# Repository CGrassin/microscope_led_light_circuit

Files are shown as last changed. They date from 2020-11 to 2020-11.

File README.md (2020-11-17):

# Microscope LED Driver circuit

This circuit drives a 1W or 3W LED to convert old optical microscopes from light bulb/halogen lamp to LED ligthing.

It is powered from a USB type C port and is fully dimmable. It may be used with a USB power bank, for instance.

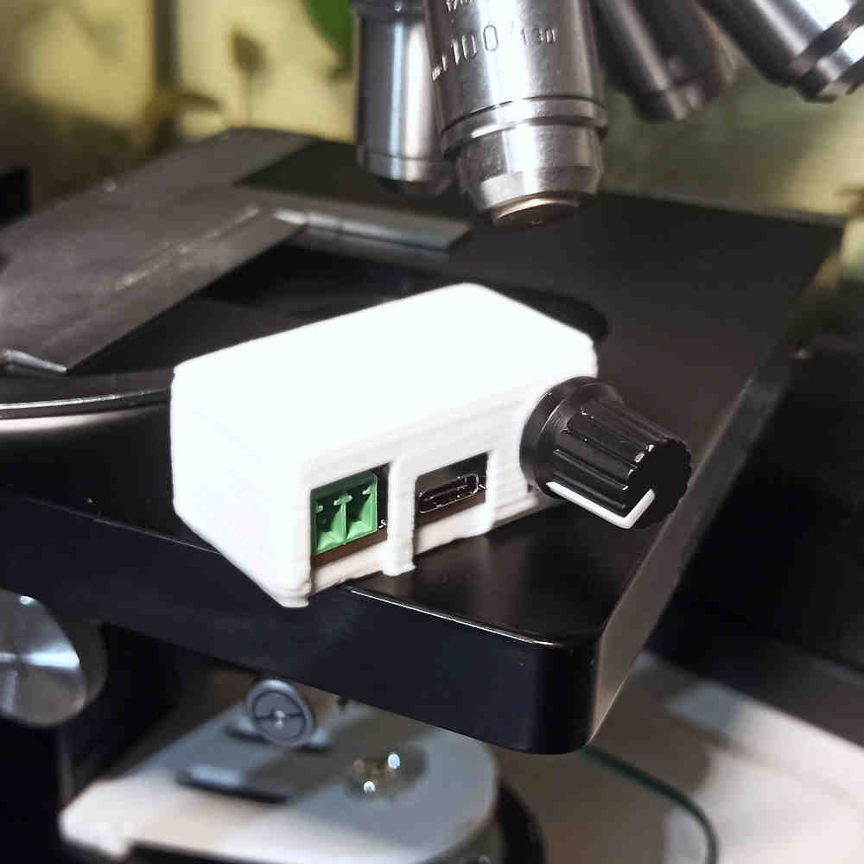
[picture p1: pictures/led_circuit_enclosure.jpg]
LED dimming circuit in its 3D printed enclosure


LEDs are considerably more efficient (i.e. less heat), have a longer lifespan and have a better color accuracy than bulbs. My circuit has a high PWM frequency to avoid flickering and rolling bands effect in photographs.

## Features

| Specification  | Value                                     |
|:---------------|:------------------------------------------|
| Power input    | 5V @ 1A max. (USB type C)                 |
| PWM frequency  | >8KHz                                     |
| Controls       | Combined knob dimming (0-100%) and ON/OFF |
| Estimated cost | About $10                                 |

## Build instructions

Gerber files are ready to upload to your prefered PCB manufacturer. The components are generic and should be available at most electronic components distributors. I personally use JLCPCB and LCSC.

Hand soldering this board is easy. I included an "interactive BOM" to help with part placement.

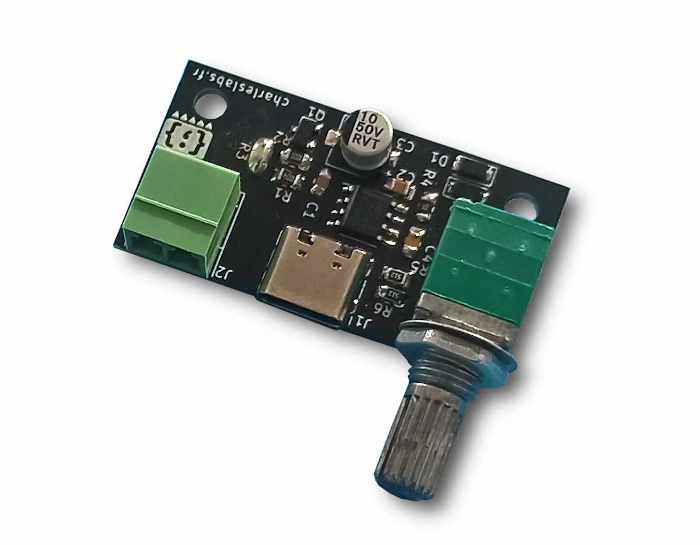
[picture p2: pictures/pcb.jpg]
This project's PCB fully assembled


The only additional required parts are a 1W or 3W "star" LED with a 30° lens to pre-focus the light into the condenser. Thank to this lens, a 1W LED is sufficient. You can choose your favorite color temperature.

I also included a 3D-printable case for the circuit. Print at 0.2mm layer height, no support required.

*Although I designed a PCB, this circuit could be build on a piece of stripboard or even breadboard.*

## Principle of operation

This circuit uses a classic 555 variable duty cycle astable multivibrator configuration.

The potentiometer adjusts the charge and discharge rate of the TRIG capacitor. The frequency of the carrier depend on the RC constant of those parts.

## License

All files in this repository are released under CC-BY license.

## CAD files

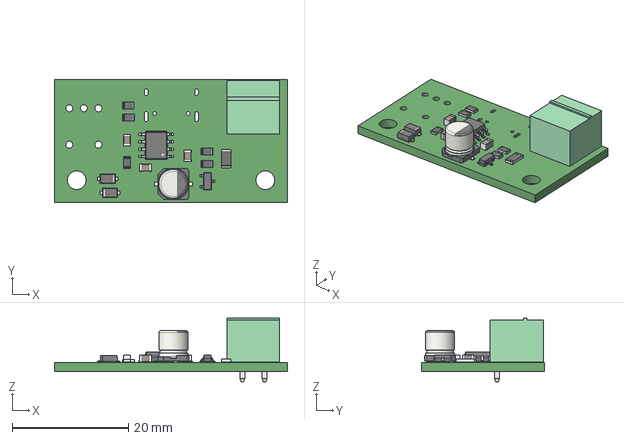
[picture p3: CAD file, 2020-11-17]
Microscope_LED_light_enclosure/Microscope_LED.step
40.0 x 21.1 x 10.9 mm

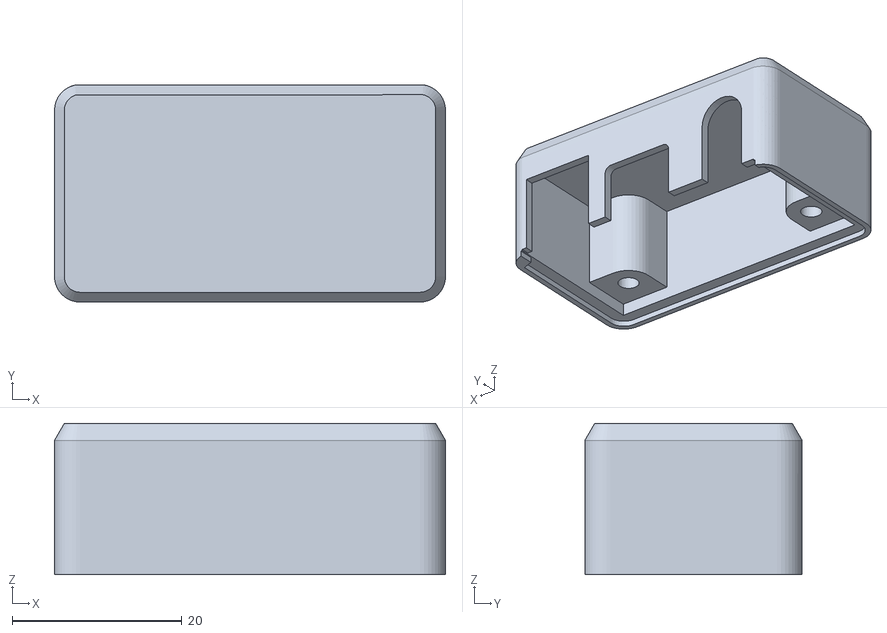
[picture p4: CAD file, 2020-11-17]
Microscope_LED_light_enclosure/Microscope_LED-TOP.STL
46.0 x 25.6 x 17.8

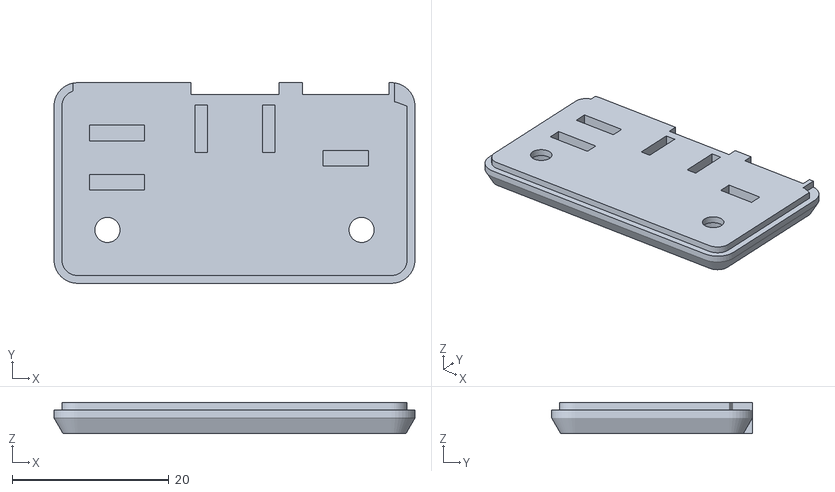
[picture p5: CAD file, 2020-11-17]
Microscope_LED_light_enclosure/Microscope_LED-BASE.STL
46.0 x 25.6 x 4.00

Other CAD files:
Microscope_LED_light_enclosure/Microscope_LED.SLDPRT

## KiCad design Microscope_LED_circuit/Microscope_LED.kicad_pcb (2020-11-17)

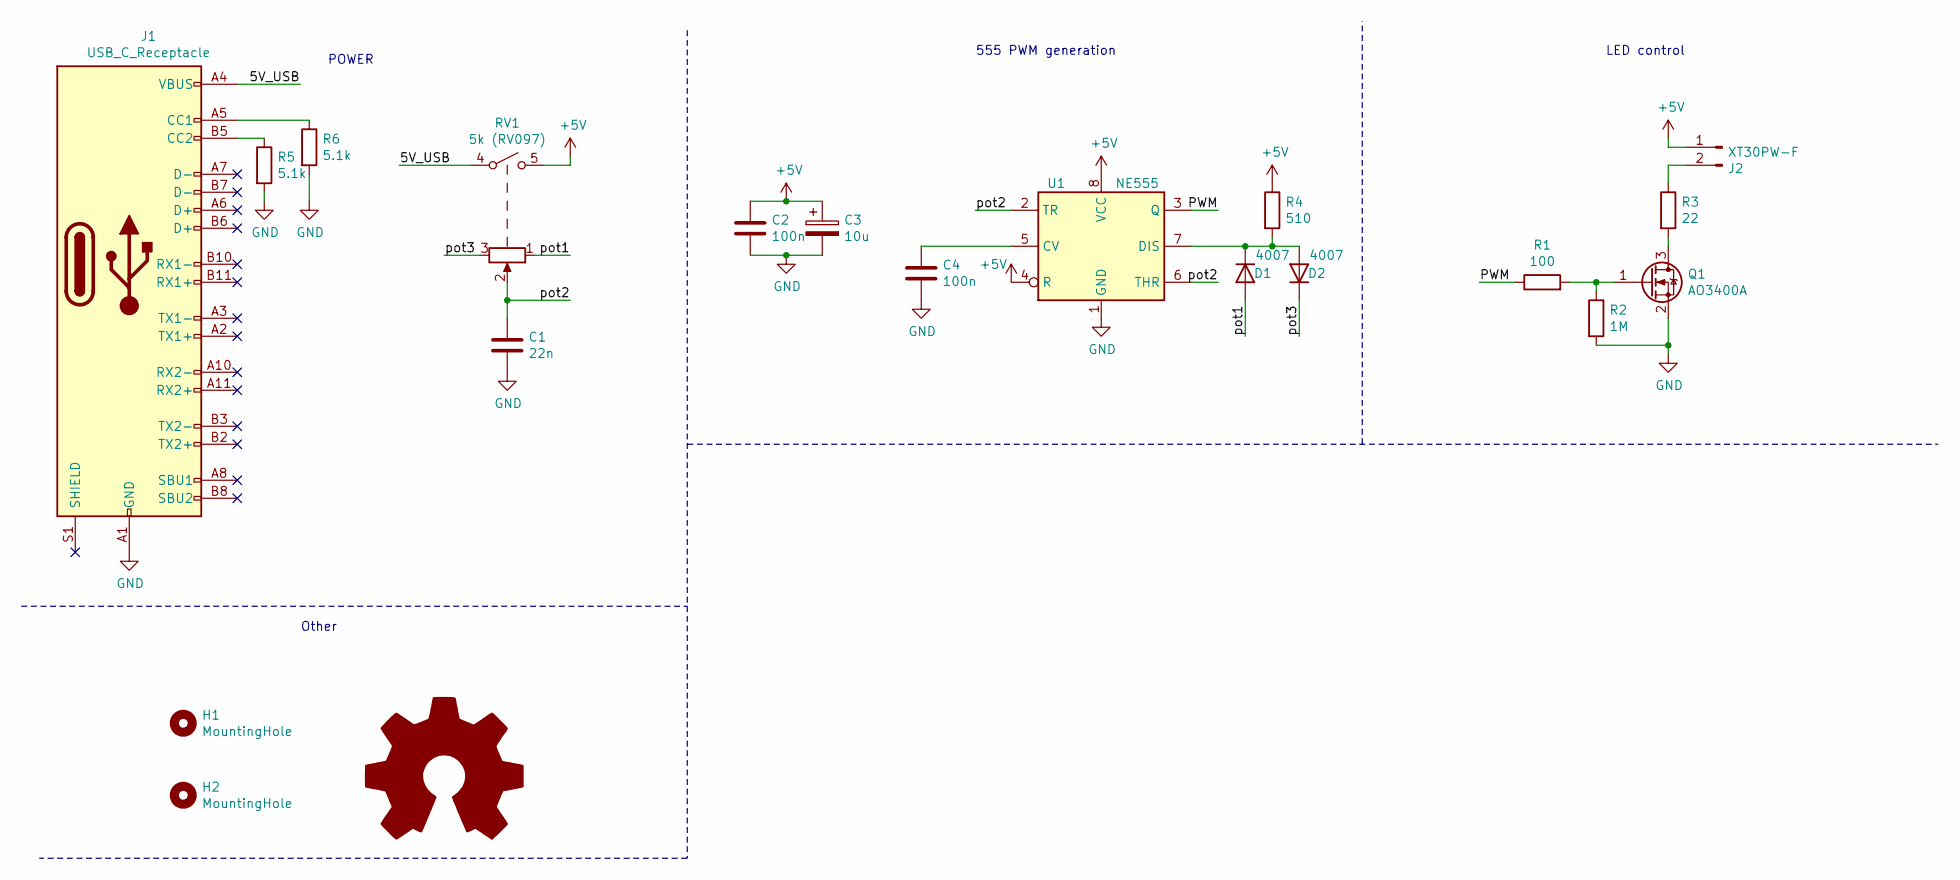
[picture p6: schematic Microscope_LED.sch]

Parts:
C1: 22n; C_0805_2012Metric_Pad1.15x1.40mm_HandSolder; LCSC C282752
C2, C4: 100n; C_0805_2012Metric_Pad1.15x1.40mm_HandSolder; LCSC C476766
C3: 10u; CP_Elec_5x5.4; LCSC C72487
D1, D2: 4007; D_SOD-123F; LCSC C108803
H1, H2: MountingHole; MountingHole_3.2mm_M3
J1: USB_C_Receptacle; USB_C_Receptacle_HRO_TYPE-C-31-M-12; LCSC C393939
J2: XT30PW-F; PhoenixContact_MC_1,5_2-G-3.81_1x02_P3.81mm_Horizontal; LCSC C8387
LOGO1: Logo_Open_Hardware_Large; Charleslabs_Logo_5mm
Q1: AO3400A; SOT-23; LCSC C122850
R1: 100; R_0805_2012Metric_Pad1.15x1.40mm_HandSolder; LCSC C17408
R2: 1M; R_0805_2012Metric_Pad1.15x1.40mm_HandSolder; LCSC C17514
R3: 22; R_1206_3216Metric
R4: 510; R_0805_2012Metric_Pad1.15x1.40mm_HandSolder; LCSC C25317
R5, R6: 5.1k; R_0805_2012Metric_Pad1.15x1.40mm_HandSolder; LCSC C115337
RV1: 5k (RV097); RV097
U1: NE555; SOIC-8_3.9x4.9mm_P1.27mm; LCSC C7593

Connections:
+5V: C2.1, C3.1, J2.1, R4.1, RV1.5, U1.4 (R), U1.8 (VCC)
/5V_USB: J1.A4 (VBUS), J1.A9 (VBUS), J1.B4 (VBUS), J1.B9 (VBUS), RV1.4
/PWM: R1.1, U1.3 (Q)
/pot1: D1.2 (A), RV1.1
/pot2: C1.1, RV1.2, U1.2 (TR), U1.6 (THR)
/pot3: D2.1 (K), RV1.3
GND: C1.2, C2.2, C3.2, C4.2, J1.A1 (GND), J1.A12 (GND), J1.B1 (GND), J1.B12 (GND), Q1.2 (S), R2.2, R5.2, R6.2, U1.1 (GND)
unnamed: C4.1, U1.5 (CV)
unnamed: D1.1 (K), D2.2 (A), R4.2, U1.7 (DIS)
unnamed: J1.A5 (CC1), R6.1
unnamed: J1.B5 (CC2), R5.1
unnamed: J2.2, R3.1
unnamed: Q1.1 (G), R1.2, R2.1
unnamed: Q1.3 (D), R3.2

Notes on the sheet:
POWER
555 PWM generation
LED control
Other

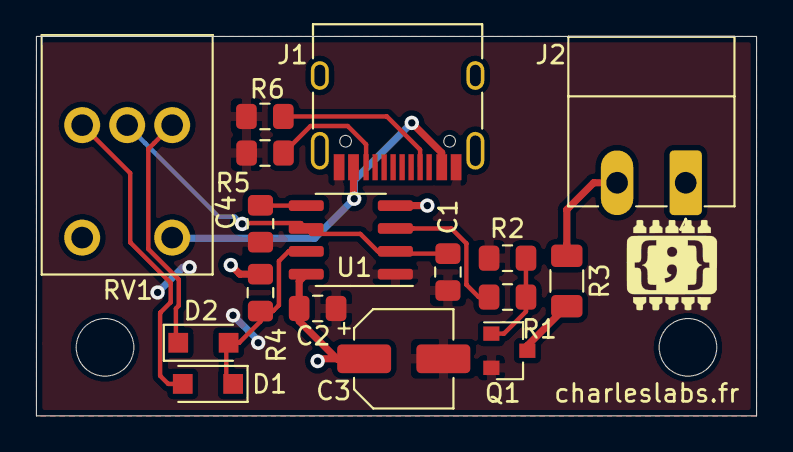
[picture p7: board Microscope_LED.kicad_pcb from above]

Board: 2 copper layers, 40.0 x 21.1 mm, 20 parts (0 on the bottom side), 14 nets.

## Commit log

2020-11-17 Release PCB rev. 1
    [Microscope_LED-B_Cu.gbr, Microscope_LED-B_Mask.gbr, Microscope_LED-B_Paste.gbr, Microscope_LED-B_SilkS.gbr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]
2020-11-17 Release PCB rev. 2
    [Microscope_LED-B_Cu.gbr, Microscope_LED-B_Mask.gbr, Microscope_LED-B_Paste.gbr, Microscope_LED-B_SilkS.gbr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]
